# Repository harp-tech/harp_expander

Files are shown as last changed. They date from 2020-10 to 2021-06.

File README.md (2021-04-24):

# Harp Input Expander
# Harp Output Expander

Harp board to expand the inputs and outputs of the current harp ecosystem.

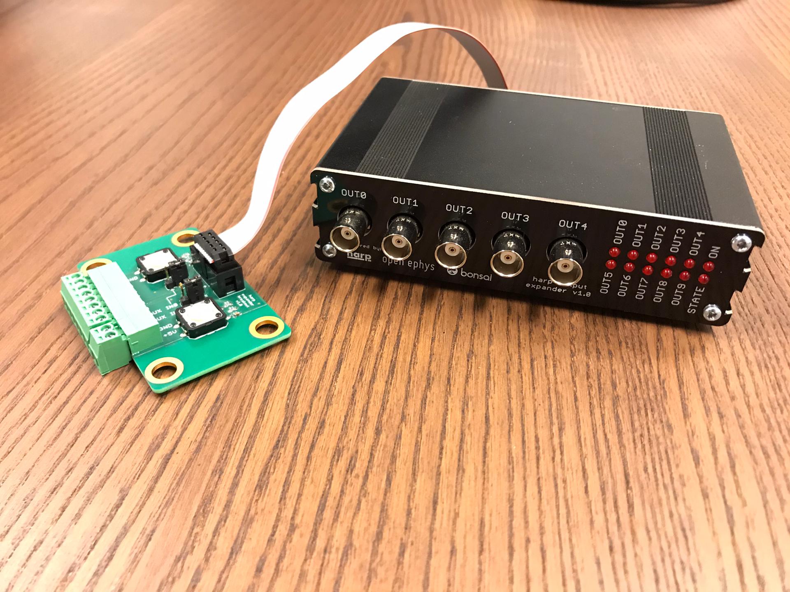
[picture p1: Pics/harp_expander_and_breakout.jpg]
DeviceFront


# Licensing

The code, designs, documentation, and photos available in this repository is free: you can redistribute it and/or modify it under the terms of the used license.
Each subdirectory will contain a license or, possibly, a set of licenses if it involves both hardware and software. Check files named LICENSE.

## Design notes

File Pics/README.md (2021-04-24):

### Licensing
Copyright Filipe Carvalho 2021

<br />Este trabalho está licenciado com uma Licença <a rel="license" href="http://creativecommons.org/licenses/by/4.0/">Creative Commons - Atribuição  4.0 Internacional</a>.

#### You are free to:
*Share* — copy and redistribute the material in any medium or format.

*Adapt* — remix, transform, and build upon the material for any purpose, even commercially.

#### Under the following terms:
*Attribution* — You must give appropriate credit, provide a link to the license, and indicate if changes were made. You may do so in any reasonable manner, but not in any way that suggests the licensor endorses you or your use.

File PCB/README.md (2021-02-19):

# Harp Expander PCB

## Licensing

The designs, documentation, and photos available in this repository are free: you can redistribute it and/or modify it under the terms of the used license.
Check file named LICENSE.

Copyright Filipe Carvalho 2020-2021

<br />This work is licensed under a <a rel="license" href="http://creativecommons.org/licenses/by-nc-sa/3.0/igo/">Creative Commons Attribution-NonCommercial-ShareAlike 3.0 IGO License</a>.

If your are interested in obtaining a license to sell this device, please contact filipe@open-ephys.org

[1]: https://docs.google.com/spreadsheets/d/1aobmmEzBDethzIlrm1eg0eYkBqlyX3s9WbA9KgRwVQI/edit?usp=sharing

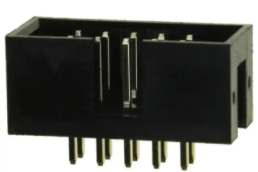
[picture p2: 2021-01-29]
PCB modules/magnetic encoder/mechanical/bottom's connector.bmp

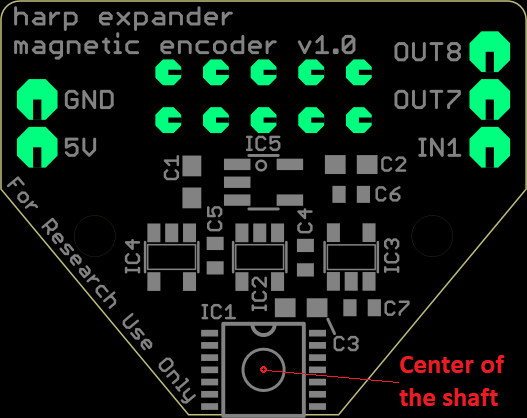
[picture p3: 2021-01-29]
PCB modules/magnetic encoder/mechanical/shaft center.bmp

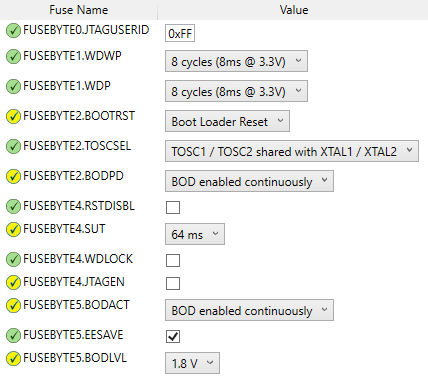
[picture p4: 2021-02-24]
Firmware/Releases/FusesATxmega128A1U (atmel studio 7).bmp

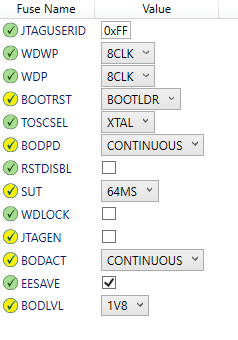
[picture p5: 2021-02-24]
Firmware/Releases/FusesATxmega128A1U.bmp

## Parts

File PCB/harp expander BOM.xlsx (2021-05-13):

Qty | Value | Package | Parts | MPN | Type
PCB COMPONENTS
5 | BNC plug |  | BNC0, BNC1, BNC2, BNC3, BNC4 | 73100-0105 | TH
27 | 100nF | C0402 | C1, C3, C5, C7, C9, C12, C13, C14, C15, C16, C17, C18, C19, C20, C21, C22, C25, C26, C27, C28, C29, C30, C31, C32, C35, C36, C40 | MC0402B104K160CT | SMD
9 | 4.7uF | C0603 | C10, C11, C23, C24, C33, C34, C37, C38, C52 | C1608X6S1C475K080AC | SMD
1 | 4.7nF | C0402 | C2 | 885012205084 | SMD
1 | 100u 25V | TT2D6 | C39 | EEUFM1E101B | TH
2 | 47pF | C0402 | C4, C6 | 04025A470JAT2A | SMD
11 | 330pF | C0402 | C41, C42, C43, C44, C45, C46, C47, C48, C49, C50, C51 | C0402C331J5GACTU | SMD
2 | CLCK_JACK | 35RASMT2BHNTRX | CLKIN, CLKOUT | 35RASMT2BHNTRX | SMD
1 | XMEGA-A1TQFP | TQFP100 | IC1 | ATXMEGA128A1U-AU | SMD
1 | USBLC6-2SC6 | SOT23-6L | IC2 | USBLC6-2SC6 | SMD
1 | FT232RL | SSOP28 | IC3 | FT232RL-REEL | SMD
2 | TLV70033DDCR | TSOT23-5 | IC4, IC5 | TLV70033DDCR | SMD
1 | SI8610BC-B-IS | SO-08 | IC6 | SI8610EC-B-IS | SMD
4 | SN74LVC1G125DBVT | SOT23-5 | IC7, IC8, IC9, IC10 | SN74LVC1G125DBVT | SMD
1 | 40R@100MHz | R0805 | L1 | MI0805K400R-10 | SMD
6 | RED_LEDs | 569-011X-X00_LED_ARRAY | LED0, LED1, LED2, LED3, LED4, LED5 | 5690-111-100F | TH
1 | Oscillator | OSCILLATOR_3.2X2.5 | OSC | O 32,0-JT32C-A-K-3,3-LF | SMD | Alternative: DSC1001CI5-032.0000T
1 | PROG HEADER | MA03-2 | PDI | 67996-206HLF | TH
1 | 10R | R0402 | R2 | CRCW040210R0FKEDHP | SMD
12 | 1k | R0402 | R20, R21, R22, R23, R24, R25, R26, R27, R28, R29, R30, R31 | CRCW04021K00FKED | SMD
31 | 10k | R0402 | R3, R9, R10, R11, R12, R13, R14, R15, R16, R17, R19, R38, R43, R46, R47, R53, R54, R55, R56, R57, R58, R59, R60, R61, R62, R63, R64, R65, R66, R67, R68 | CRCW040210K0FKED | SMD
12 | 330R | R0402 | R32, R33, R34, R35, R36, R37, R39, R40, R41, R42, R44, R45 | RC0402FR-07330RL | SMD
11 | 100R | R0603 | R4, R5, R6, R7, R8, R48, R49, R50, R51, R52, R69 | CRCW0603100RFKEAHP | SMD
1 | I/O Header | ML10L | SV1 | SBH11-PBPC-D05-RA-BK | TH
12 | BC850 | SOT23 | T2, T3, T4, T5, T6, T7, T8, T9, T10, T11, T12, T13 | BC850C,215 | SMD
2 | 744245X | SO24L | U1, U2 | 74LVC4245AD,118 | SMD
1 | 74HCT125SO14 | SO14 | U3 | 74HCT125D,653 | SMD
1 | mini USB | 240-0002-1 | USB | UX60-MB-5S8 | SMD
1 |  |  | PCB
POST-PRODUCTION
1 |  |  | Front Panel PCB | PCBWAY
1 |  |  | Rear Panel PCB | PCBWAY
1 |  |  | Enclosure | B5-080BK
4 |  |  | Bumper Cylindrical Dome 9.53mm | SJ-5306-CLEAR-3000/CASE
ACCESSORIES
1 |  |  | 3.5mm stereo jack cable 1.2 m, Black | AV13646
1 |  |  | 0.9 left angle USB cable | USB2HABM3RA
NOTES
 |  |  |  | Number of unique parts | 28
 |  |  |  | Number of unique SMD parts | 23
 |  |  |  | Number of unique TH parts | 5
 |  |  |  | Number of SMD parts | 147
 |  |  |  | Number of TH parts | 14
 |  | Optional
 |  | Holder: MF80BK2

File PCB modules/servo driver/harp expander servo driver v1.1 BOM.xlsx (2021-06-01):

Qty | Value | Package | Parts | MPN | Type | Distributor | Distributor PN
ASSEMBLY HOUSE
2 | SI8641AB-B-IS | SO16W | U1, U2 | SI8641AB-B-IS | SMD | Digikey | SI8641AB-B-IS-ND
1 | LT1765 | TSSOP16 | U3 | LT1765EFE#TRPBF | SMD | Digikey | LT1765EFE#TRPBFCT-ND
1 | NCP718XSN500 | SOT23-5 | U4 | NCP718BSN500T1G | SMD | Digikey | NCP718BSN500T1GOSCT-ND
6 | 100nF | C0402 | C1, C2, C3, C4, C5, C6 | CGA2B3X7R1H104K050BB | SMD | Digikey | 445-6899-2-ND
1 | 10uF | C0603 | C10 | EMK107BBJ106MA-T | SMD | Digikey | 587-3238-1-ND
2 | 2.2uF | C0603 | C7, C11 | GRM188R61E225MA12D | SMD | Digikey | 490-12738-1-ND
1 | 2.2nF | C0402 | C8 | CL05B222JB5NNNC | SMD | Digikey | 1276-1532-6-ND
1 | 180nF | C0603 | C9 | GCG188R91H184KA01D | SMD | Digikey | 490-GCG188R91H184KA01DCT-ND
1 | 40.2k | R0402 | R1 | RC0402FR-0740K2L | SMD | Digikey | 311-40.2KLRCT-ND
2 | 10k | R0402 | R2, R3 | CRCW040210K0FKEDC | SMD | Digikey | 541-3959-1-ND
1 | SSB43L-E3 | SMB | D1 | SSB43L-E3/52T | SMD | Digikey | SSB43L-E3/52TGICT-ND
1 | CMDSH-3 | SOD323-R | D2 | CMDSH-3 | SMD | Digikey | 1514-CMDSH-3TRPBFREECT-ND
1 | 10uH 3A | COILCRAFT_1 | L3 | IHLP2525CZER100M01 | SMD | Digikey | 541-1013-2-ND
1 | DC_JACK2.1MM | DC_POWER_INPUT_2.1MM | PWR1 | 163-179PH-EX | TH | Mouser | 163-179PH-EX
3 | CON_3.5MM_1X3 | CON_3.5MM_1X3 | X1, X2, X3 | 691322110003 | TH | Digikey | 732-2770-ND
1 | aux_header | FE06 | X4 | n.a. | - | - | n.a.
1 | IDC 10WAY STRAIGHT | PAK100/2500-10 | X5 | SBH11-PBPC-D05-ST-BK | TH | Digikey | S9169-ND
POST-PRODUCTION
3 | TERMINAL BLOBK PLUG 3WAY | - | n.a. | 691361100003 | - | Digikey | 732-2752-ND | to build step motor cable
2 | CNTR PLRZD RECPT 10P | - | n.a. | 1658621-1 | - | Digikey | AKC10H-ND | to build 0.5m control cable
1 | 10 COND. 28AWG ROUND 1PC=100FT | - | n.a. | 3365/10 100 | - | Digikey | 3M157849-100-ND | to build 0.5m control cable
NOTES
 |  |  |  | Number of unique parts | 16
 |  |  |  | Number of SMD parts | 21
 |  |  |  | Number of TH parts | 5

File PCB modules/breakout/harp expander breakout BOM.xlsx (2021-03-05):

Qty | Value | Package | Parts | MPN | Type
ASSEMBLY HOUSE
2 | 2.2k 100mW | R0603 | R1, R2 | ERJ3GEYJ222V | SMD
2 | 4.3k 100mW | R0603 | R3, R4 | ERJ3GEYJ432V | SMD
2 | 1uF 25V | C0603 | C1, C2 | CL10A105KA8NNNC | SMD
2 | SWITCH |  | SW0, SW1 | B3F-4000 | TH
2 | JUMPER 3WAY |  | JP1, JP2 | 68001-203HLF | TH
1 | IDC 10WAY STRAIGHT |  | SV1 | SBH11-PBPC-D05-ST-BK | TH
1 | TERMINAL BLOCK 8WAY |  | SV2 | 691322110008 | TH
1 | TERMINAL BLOCK 2WAY |  | SV3 | 691322110002 | TH
POST-PRODUCTION
1 | TERMINAL BLOCK PLUG 8WAY |  |  | 691361100008
1 | TERMINAL BLOCK PLUG 2WAY |  |  | 691361100002
2 | CNTR PLRZD RECPT 10P |  |  | 1658621-1
2 | JUMPER |  |  | SNT-100-BK-T
 | 10 COND. 28AWG ROUND 1PC=100FT |  |  | 3365/10 100 |  | To create a cable with 0.5 meters
NOTES
 |  |  |  | Number of unique parts | 8
 |  |  |  | Number of SMD parts | 6
 |  |  |  | Number of TH parts | 7

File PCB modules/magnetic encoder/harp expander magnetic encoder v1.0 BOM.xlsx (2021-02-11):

Qty | Value | Package | Parts | MPN | Type | Distributor | Distributor PN
ASSEMBLY HOUSE
3 | 10uF 16V X5R 20% | C0603 | C1, C2, C3 | EMK107BBJ106MA-T | SMD | Digikey | 587-3238-6-ND
4 | 100nF 50V X7R 10% | C0402 | C4, C5, C6, C7 | CGA2B3X7R1H104K050BB | SMD | Digikey | 445-6899-6-ND
3 | Single Bus Buffer Gate | SOT-23-5 | IC2, IC3, IC4 | SN74LVC1G125DBVT | SMD | Digikey | 296-26595-6-ND
1 | Magnetic Rotary Encoder 14 bits | 14-TSSOP | IC1 | AS5048A-HTSP-500 | SMD | Digikey | AS5048A-HTSP-500DKR-ND
1 | Ultra-Low-Noise LDO 3.3V 250mA | SOT-23-5 | IC5 | LP5907MFX-3.3/NOPB | SMD | Digikey | 296-38557-6-ND
1 | IDC 10WAY STRAIGHT | PAK100/2500-10 | SV1 | SBH11-PBPC-D05-ST-BK | TH | Digikey | S9169-ND
POST-PRODUCTION
2 | CNTR PLRZD RECPT 10P |  |  | 1658621-1 | - | Digikey | AKC10H-ND
 | 10 COND. 28AWG ROUND 1PC=100FT |  |  | 3365/10 100 | - | Digikey | 3M157849-100-ND | to build 0.5m control cable
NOTES
 |  |  |  | Number of unique parts | 6
 |  |  |  | Number of SMD parts | 12
 |  |  |  | Number of TH parts | 1

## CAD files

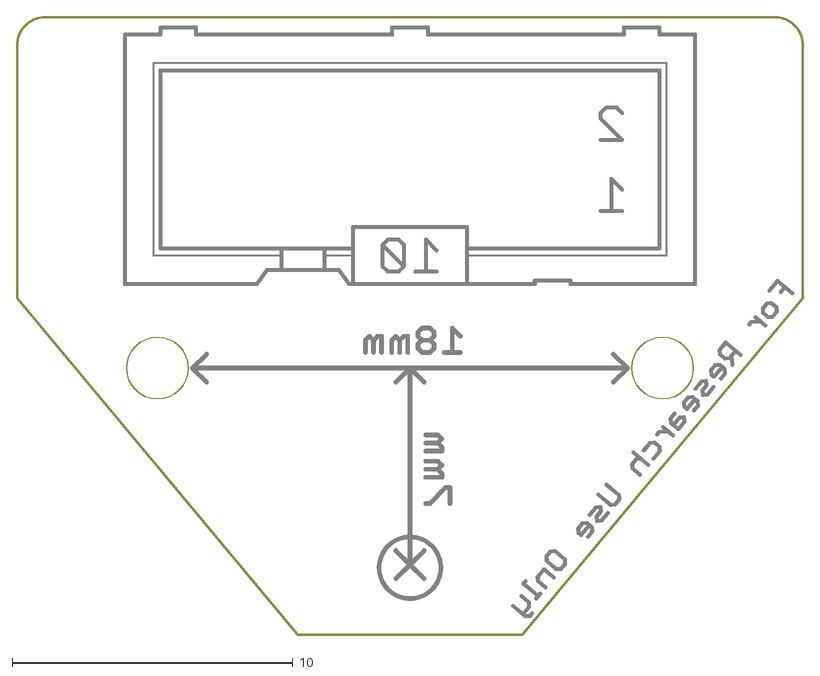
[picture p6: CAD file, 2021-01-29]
PCB modules/magnetic encoder/mechanical/harp expander magnetic encoder v1.0 - bottom.dxf
28.1 x 22.1

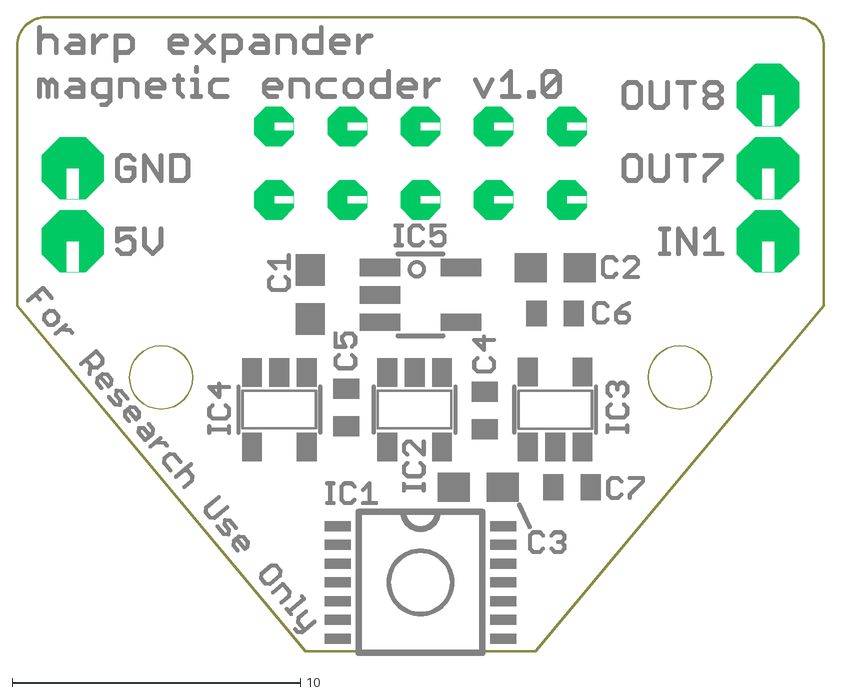
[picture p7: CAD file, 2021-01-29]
PCB modules/magnetic encoder/mechanical/harp expander magnetic encoder v1.0 - top.dxf
28.1 x 22.2

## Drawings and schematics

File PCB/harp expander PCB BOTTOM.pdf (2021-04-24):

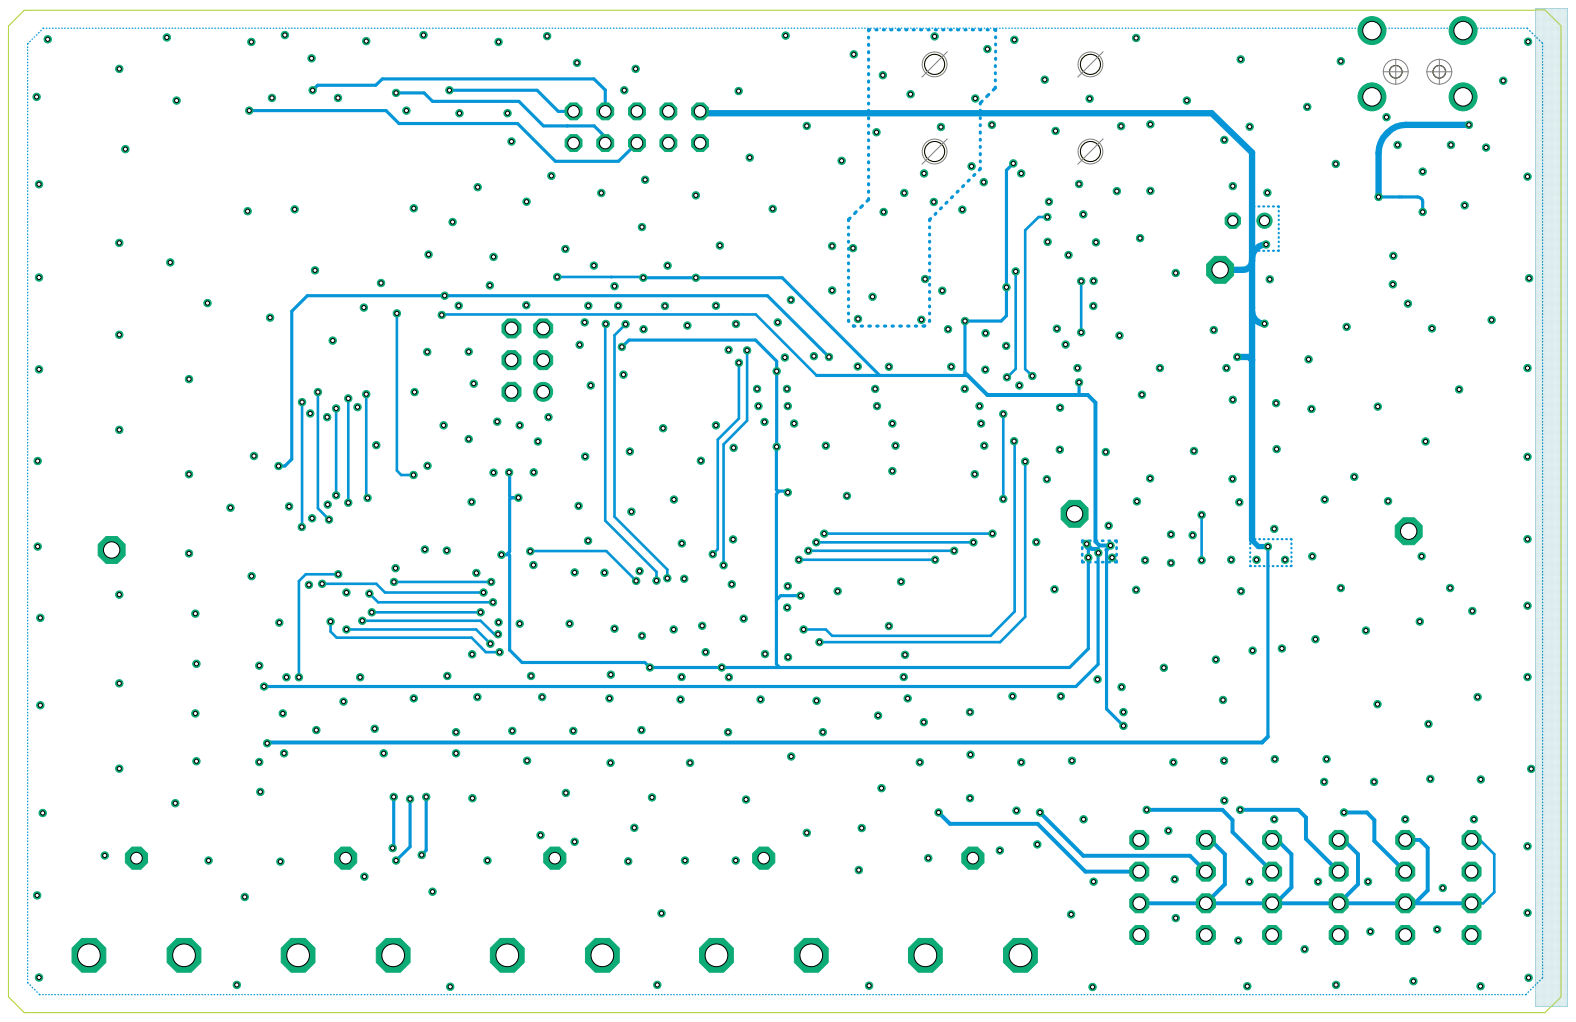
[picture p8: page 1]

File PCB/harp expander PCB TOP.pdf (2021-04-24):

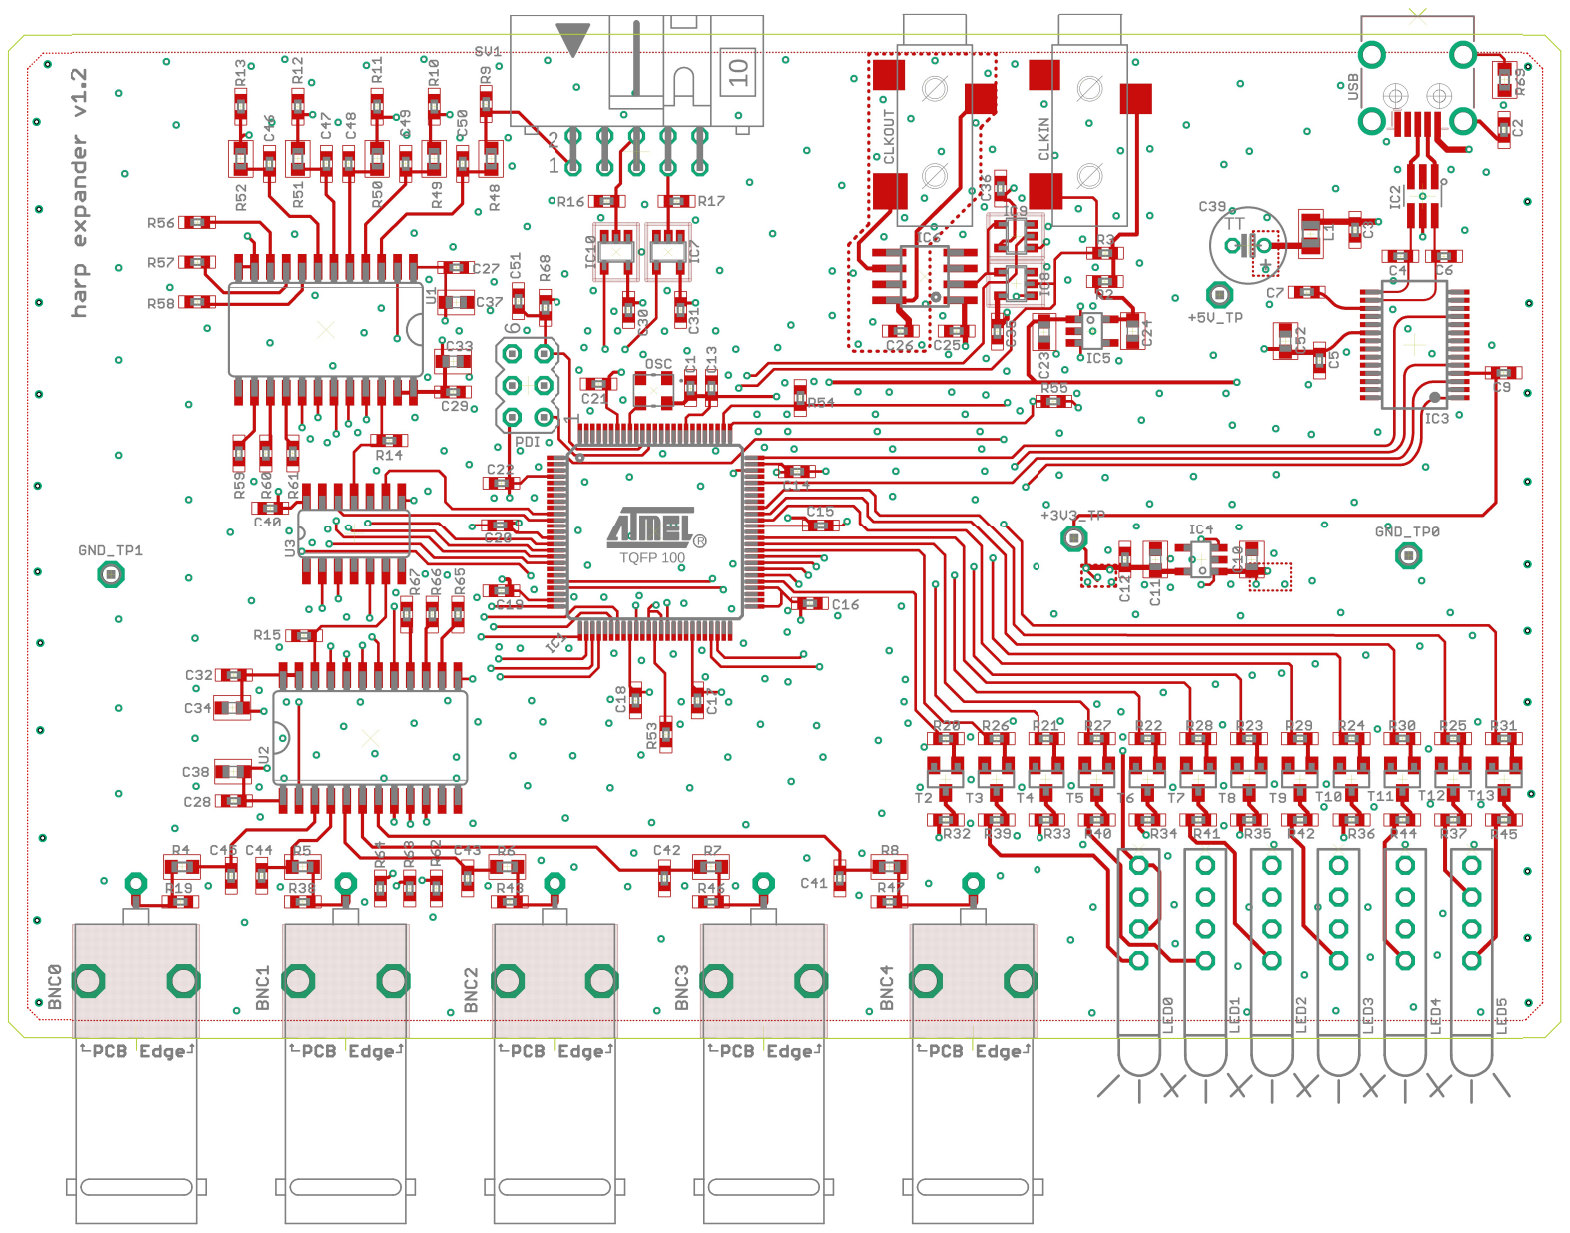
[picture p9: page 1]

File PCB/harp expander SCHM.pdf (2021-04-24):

# PF7(TXD1/SCK) 52 GND 33 GND 43

A

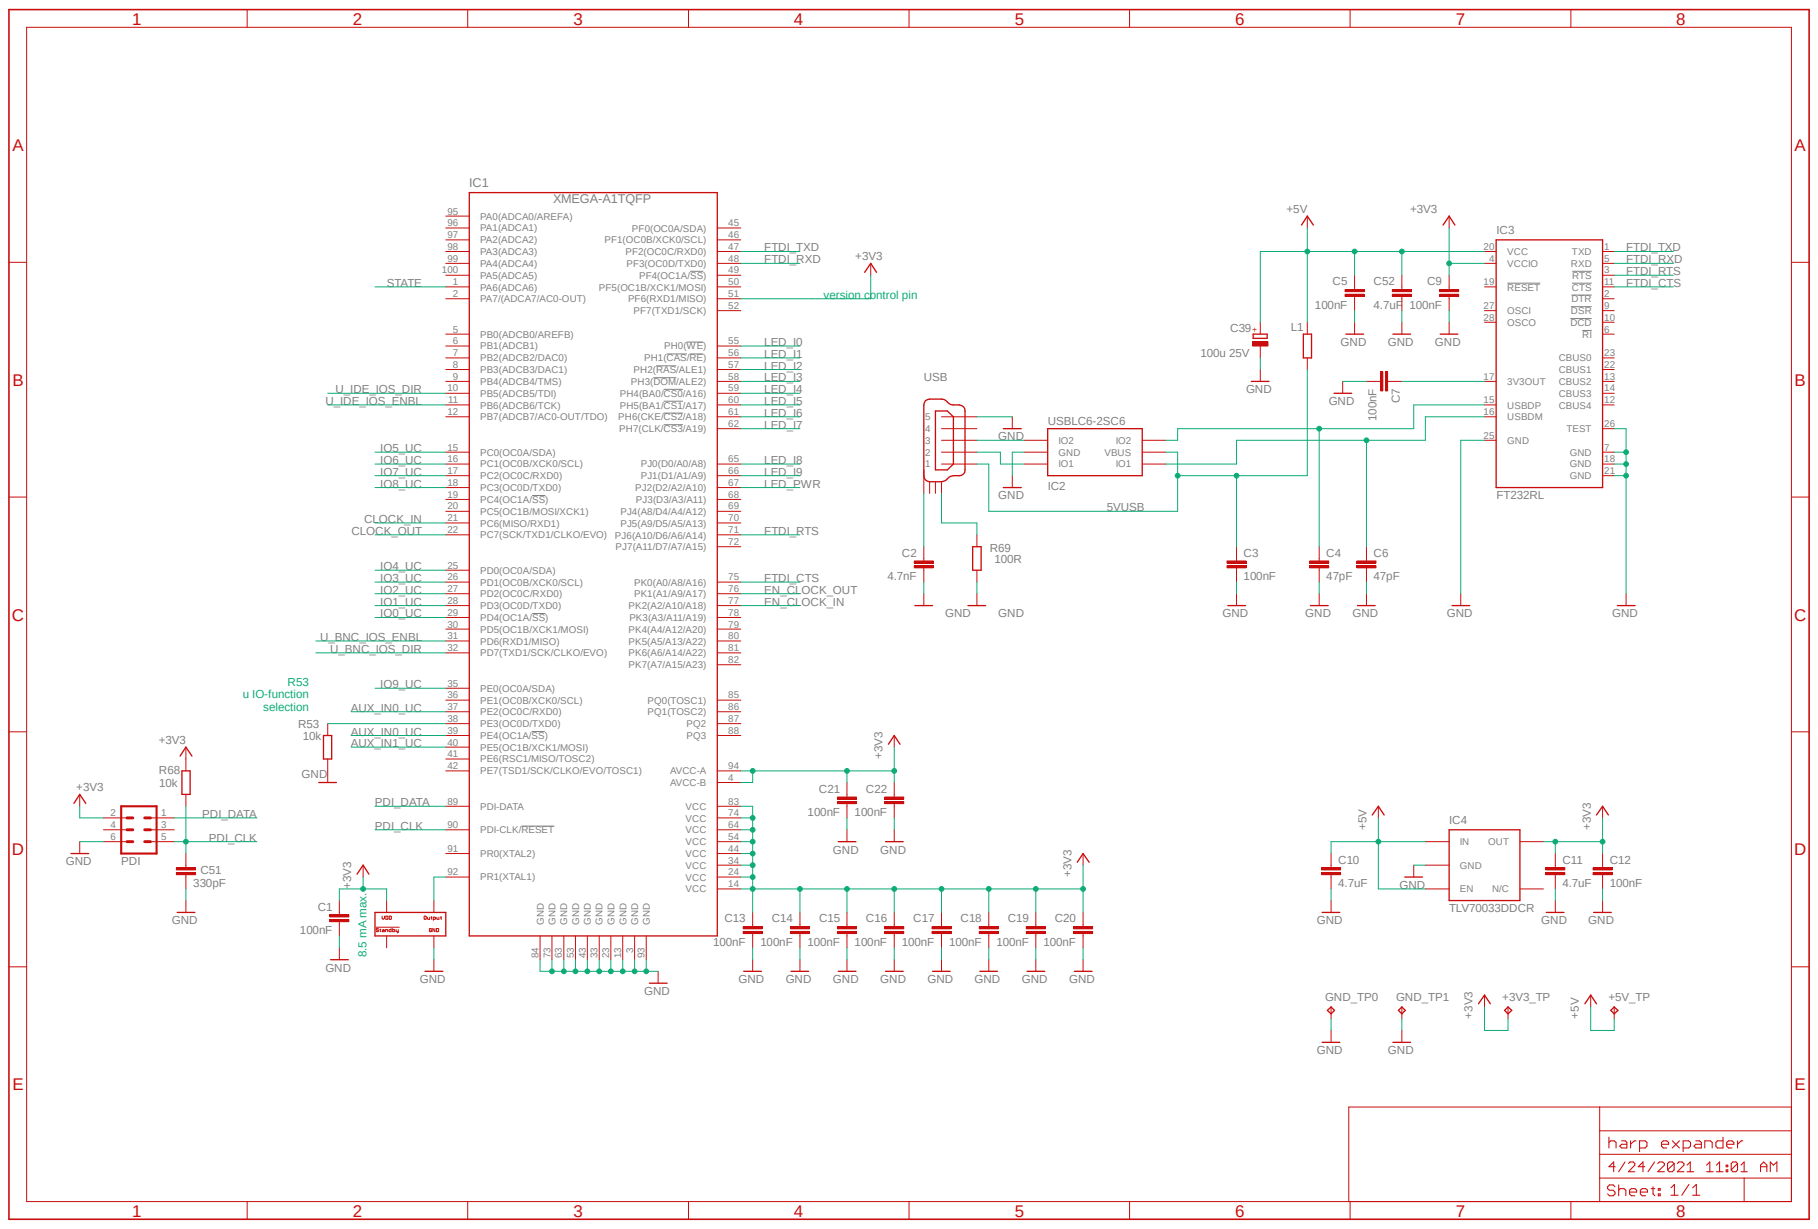
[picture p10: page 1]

A

A

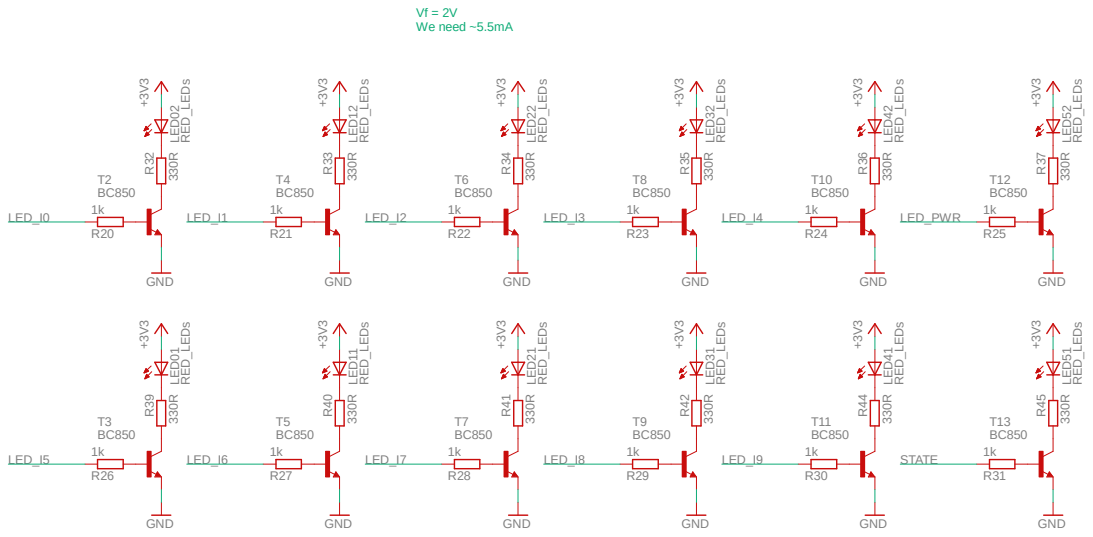
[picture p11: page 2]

A

A

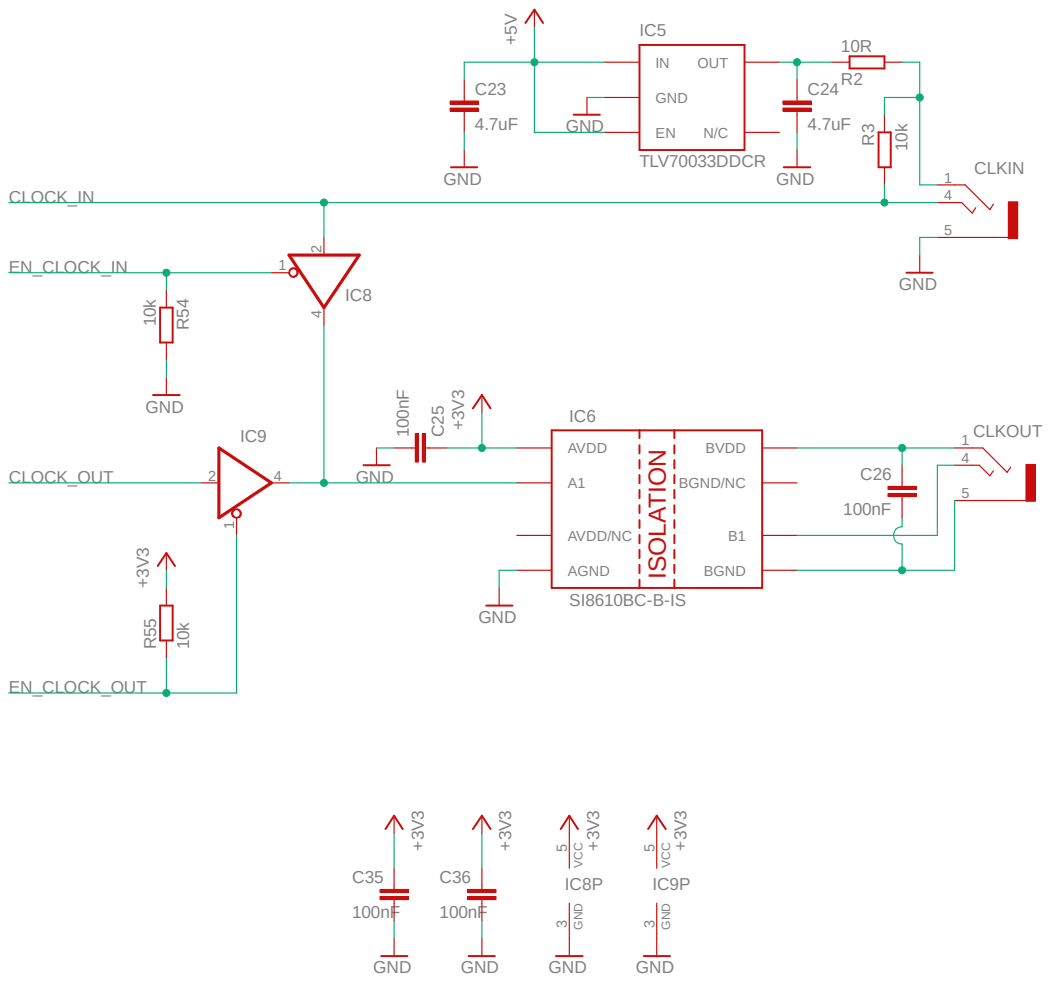
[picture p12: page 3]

# GND +3V³ +3V³

# GND 10k

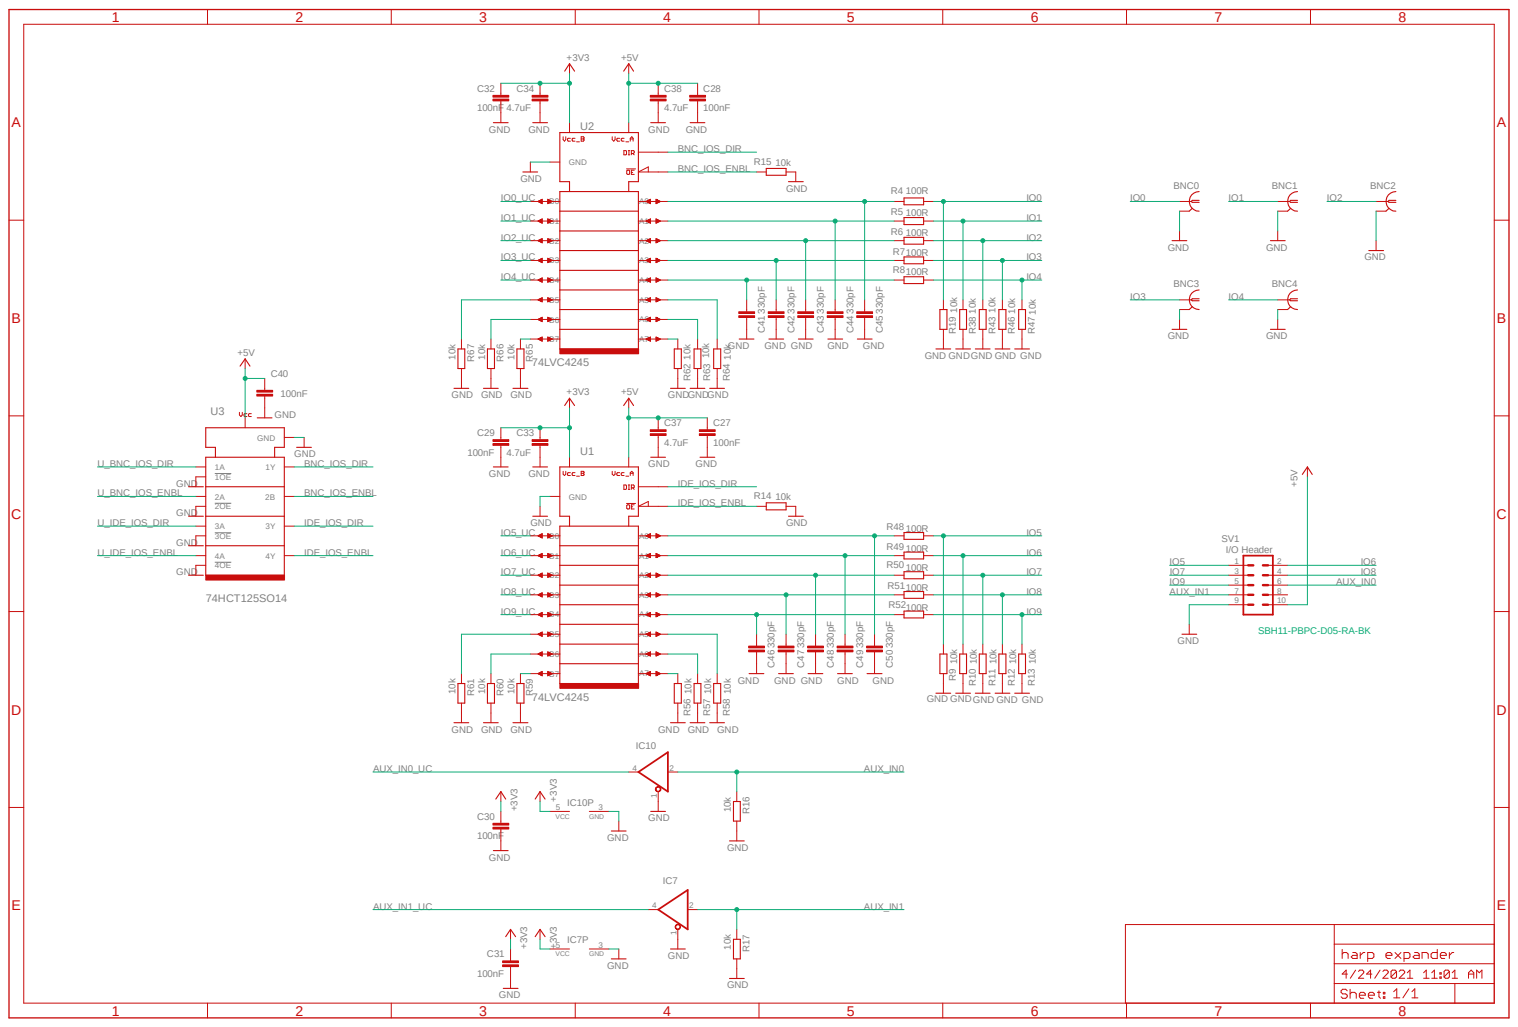
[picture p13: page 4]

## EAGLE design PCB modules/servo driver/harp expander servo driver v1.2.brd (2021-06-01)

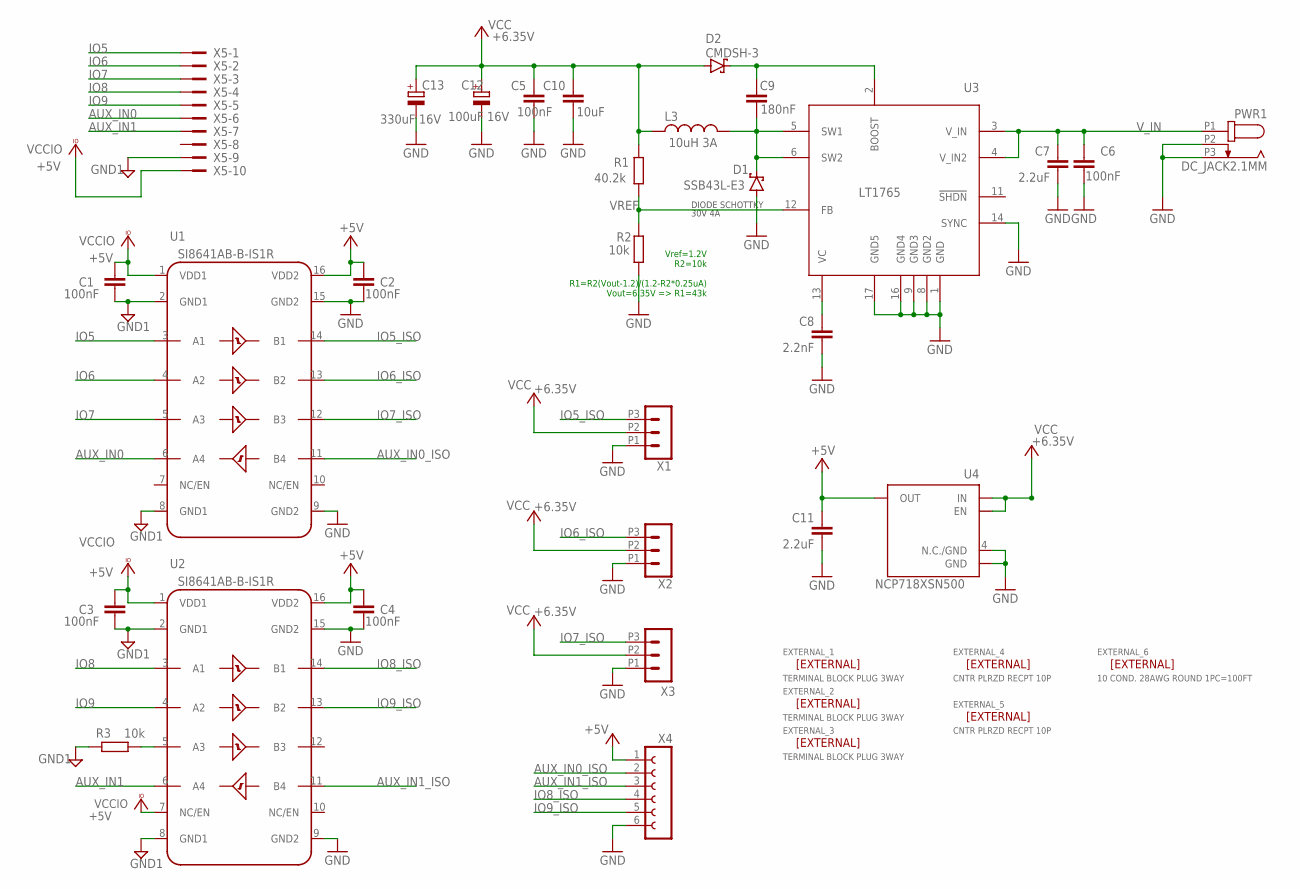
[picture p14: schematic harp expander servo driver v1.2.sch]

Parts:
C1, C2, C3, C4, C5, C6: 100nF; C0402; MPN CGA2B3X7R1H104K050BB; DIGIKEY_PN 445-6899-2-ND
C7, C11: 2.2uF; C0603; MPN GRM188R61E225MA12D; DIGIKEY_PN 490-12738-1-ND
C8: 2.2nF; C0402; MPN CL05B222JB5NNNC; DIGIKEY_PN 1276-1532-6-ND
C9: 180nF; C0603; MPN GCG188R91H184KA01D; DIGIKEY_PN 490-GCG188R91H184KA01DCT-ND
C10: 10uF; C0603; MPN EMK107BBJ106MA-T; DIGIKEY_PN 587-3238-1-ND
C12: 100uF 16V; CT7343; MPN T491D107K016AT7280; DIGIKEY_PN 399-18066-1-ND
C13: 330uF 16V; E3,5-8; MPN MCMR16V337M8X7; FARNELL_PN 1870957
D1: SSB43L-E3; SMB; MPN SSB43L-E3/52T; DIGIKEY_PN SSB43L-E3/52TGICT-ND
D2: CMDSH-3; SOD323-R; MPN CMDSH-3; DIGIKEY_PN 1514-CMDSH-3TRPBFREECT-ND
EXTERNAL_1, EXTERNAL_2, EXTERNAL_3: TERMINAL BLOCK PLUG 3WAY; -; MPN 691361100003; DIGIKEY_PN 732-2752-ND
EXTERNAL_4, EXTERNAL_5: CNTR PLRZD RECPT 10P; -; MPN 1658621-1; DIGIKEY_PN AKC10H-ND
EXTERNAL_6: 10 COND. 28AWG ROUND 1PC=100FT; -; MPN 3365/10 100; DIGIKEY_PN 3M157849-100-ND
L3: 10uH 3A; L_IHLP_PADS; MOUSER_PN 70-IHLP2525CZER100M0; DIGIKEY_PN 541-1013-2-ND
PWR1: DC_JACK2.1MM; DC_POWER_INPUT_2.1MM; MPN 163-179PH-EX; DIGIKEY_PN 163-179PH-EX MOUSER
R1: 40.2k; R0402; MPN RC0402FR-0740K2L; DIGIKEY_PN 311-40.2KLRCT-ND
R2, R3: 10k; R0402; MPN CRCW040210K0FKEDC; DIGIKEY_PN 541-3959-1-ND
U1, U2: SI8641AB-B-IS1R; SO16W; MOUSER_PN 634-SI8641AB-B-IS1R; DIGIKEY_PN SI8641AB-B-IS-ND
U3: LT1765; TSSOP16; MPN LT1765EFE#TRPBF; DIGIKEY_PN LT1765EFE#TRPBFCT-ND
U4: NCP718XSN500; SOT23-5; MPN NCP718BSN500T1G; DIGIKEY_PN NCP718BSN500T1GOSCT-ND
X1, X2, X3: CON_3.5MM_1X3; MPN 691322110003; DIGIKEY_PN 732-2770-ND
X4: aux_header; FE06; MPN n.a.
X5: IDC 10WAY STRAIGHT; PAK100/2500-10; MPN SBH11-PBPC-D05-ST-BK; DIGIKEY_PN S9169-ND

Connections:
+5V: C2.1, C4.1, C11.1, U1.16 (VDD2), U2.16 (VDD2), U4.5 (OUT), X4.1
AUX_IN0: U1.6 (A4), X5.6
AUX_IN0_ISO: U1.11 (B4), X4.2
AUX_IN1: U2.6 (A4), X5.7
AUX_IN1_ISO: U2.11 (B4), X4.3
GND: C2.2, C4.2, C5.2, C6.2, C7.2, C8.2, C10.2, C11.2, C12.-, C13.-, D1.A, PWR1.P2 (2), PWR1.P3 (3), R2.1, U1.9 (GND2), U1.15 (GND2), U2.9 (GND2), U2.15 (GND2), U3.1 (GND), U3.8 (GND2), U3.9 (GND3), U3.14 (SYNC), U3.16 (GND4), U3.17 (GND5), U4.2 (GND), U4.4 (N.C./GND), X1.P1 (1), X2.P1 (1), X3.P1 (1), X4.6
GND1: C1.2, C3.2, R3.2, U1.2 (GND1), U1.8 (GND1), U2.2 (GND1), U2.8 (GND1), X5.9
IO5: U1.3 (A1), X5.1
IO5_ISO: U1.14 (B1), X1.P3 (3)
IO6: U1.4 (A2), X5.2
IO6_ISO: U1.13 (B2), X2.P3 (3)
IO7: U1.5 (A3), X5.3
IO7_ISO: U1.12 (B3), X3.P3 (3)
IO8: U2.3 (A1), X5.4
IO8_ISO: U2.14 (B1), X4.4
IO9: U2.4 (A2), X5.5
IO9_ISO: U2.13 (B2), X4.5
unnamed: R3.1, U2.5 (A3)
unnamed: C8.1, U3.13 (VC)
unnamed: C9.2, D1.C, L3.2, U3.5 (SW1), U3.6 (SW2)
unnamed: C9.1, D2.C, U3.2 (BOOST)
VCC: C5.1, C10.1, C12.+, C13.+, D2.A, L3.1, R1.2, U4.1 (IN), U4.3 (EN), X1.P2 (2), X2.P2 (2), X3.P2 (2)
VCCIO: C1.1, C3.1, U1.1 (VDD1), U2.1 (VDD1), U2.7 (NC/EN), X5.10
VREF: R1.1, R2.2, U3.12 (FB)
V_IN: C6.1, C7.1, PWR1.P1 (1), U3.3 (V_IN), U3.4 (V_IN2)

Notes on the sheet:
Vref=1.2V R2=10k R1=R2(Vout-1.2)/(1.2-R2*0.25uA) Vout=6.35V => R1=43k
DIODE SCHOTTKY 30V 4A

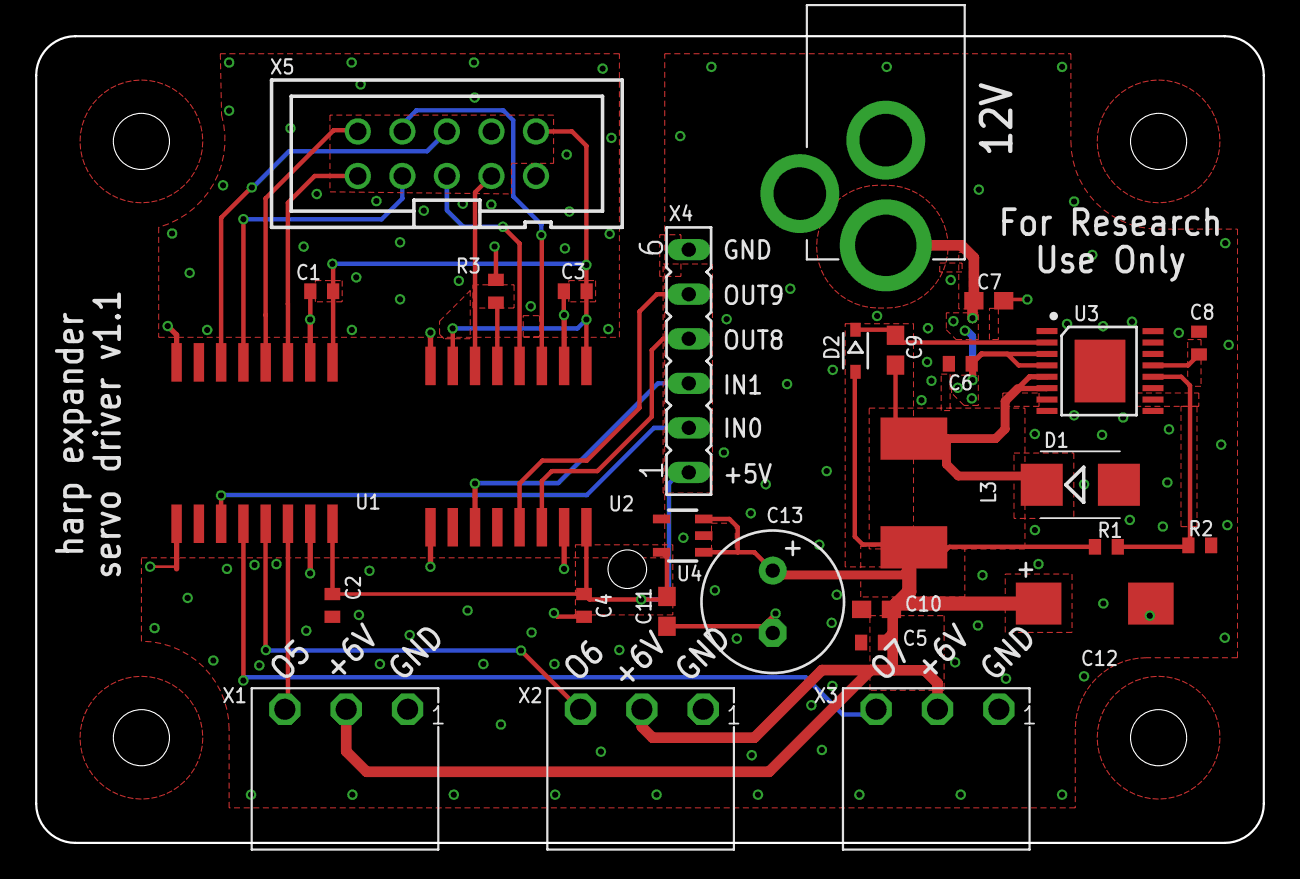
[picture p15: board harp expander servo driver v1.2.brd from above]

Board: 2 copper layers, 70.0 x 46.0 mm, 35 parts (0 on the bottom side), 25 nets.

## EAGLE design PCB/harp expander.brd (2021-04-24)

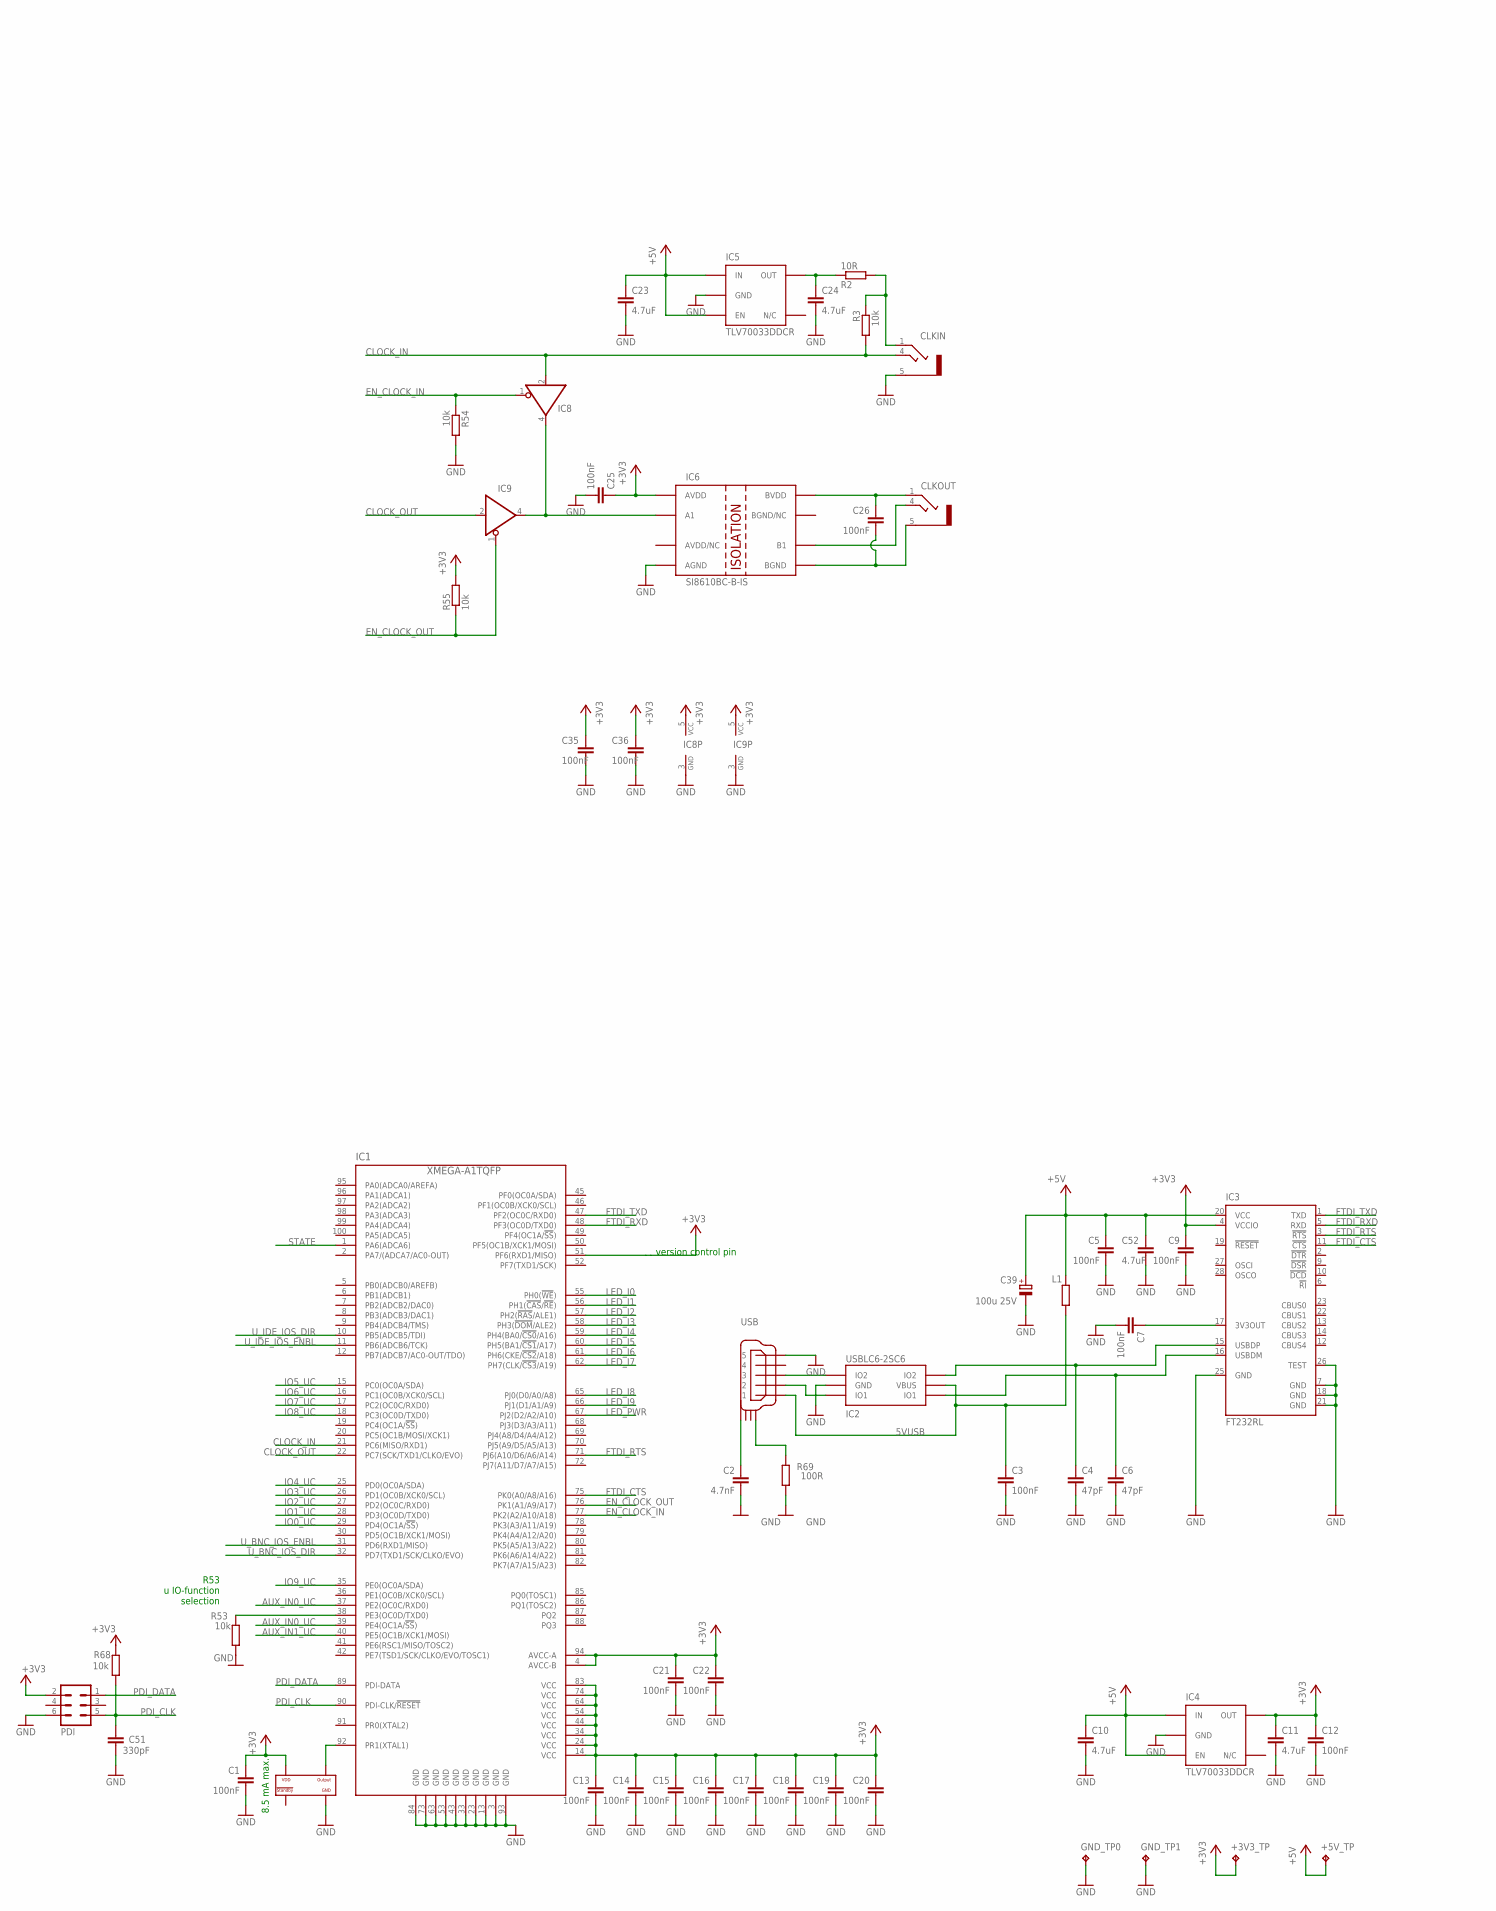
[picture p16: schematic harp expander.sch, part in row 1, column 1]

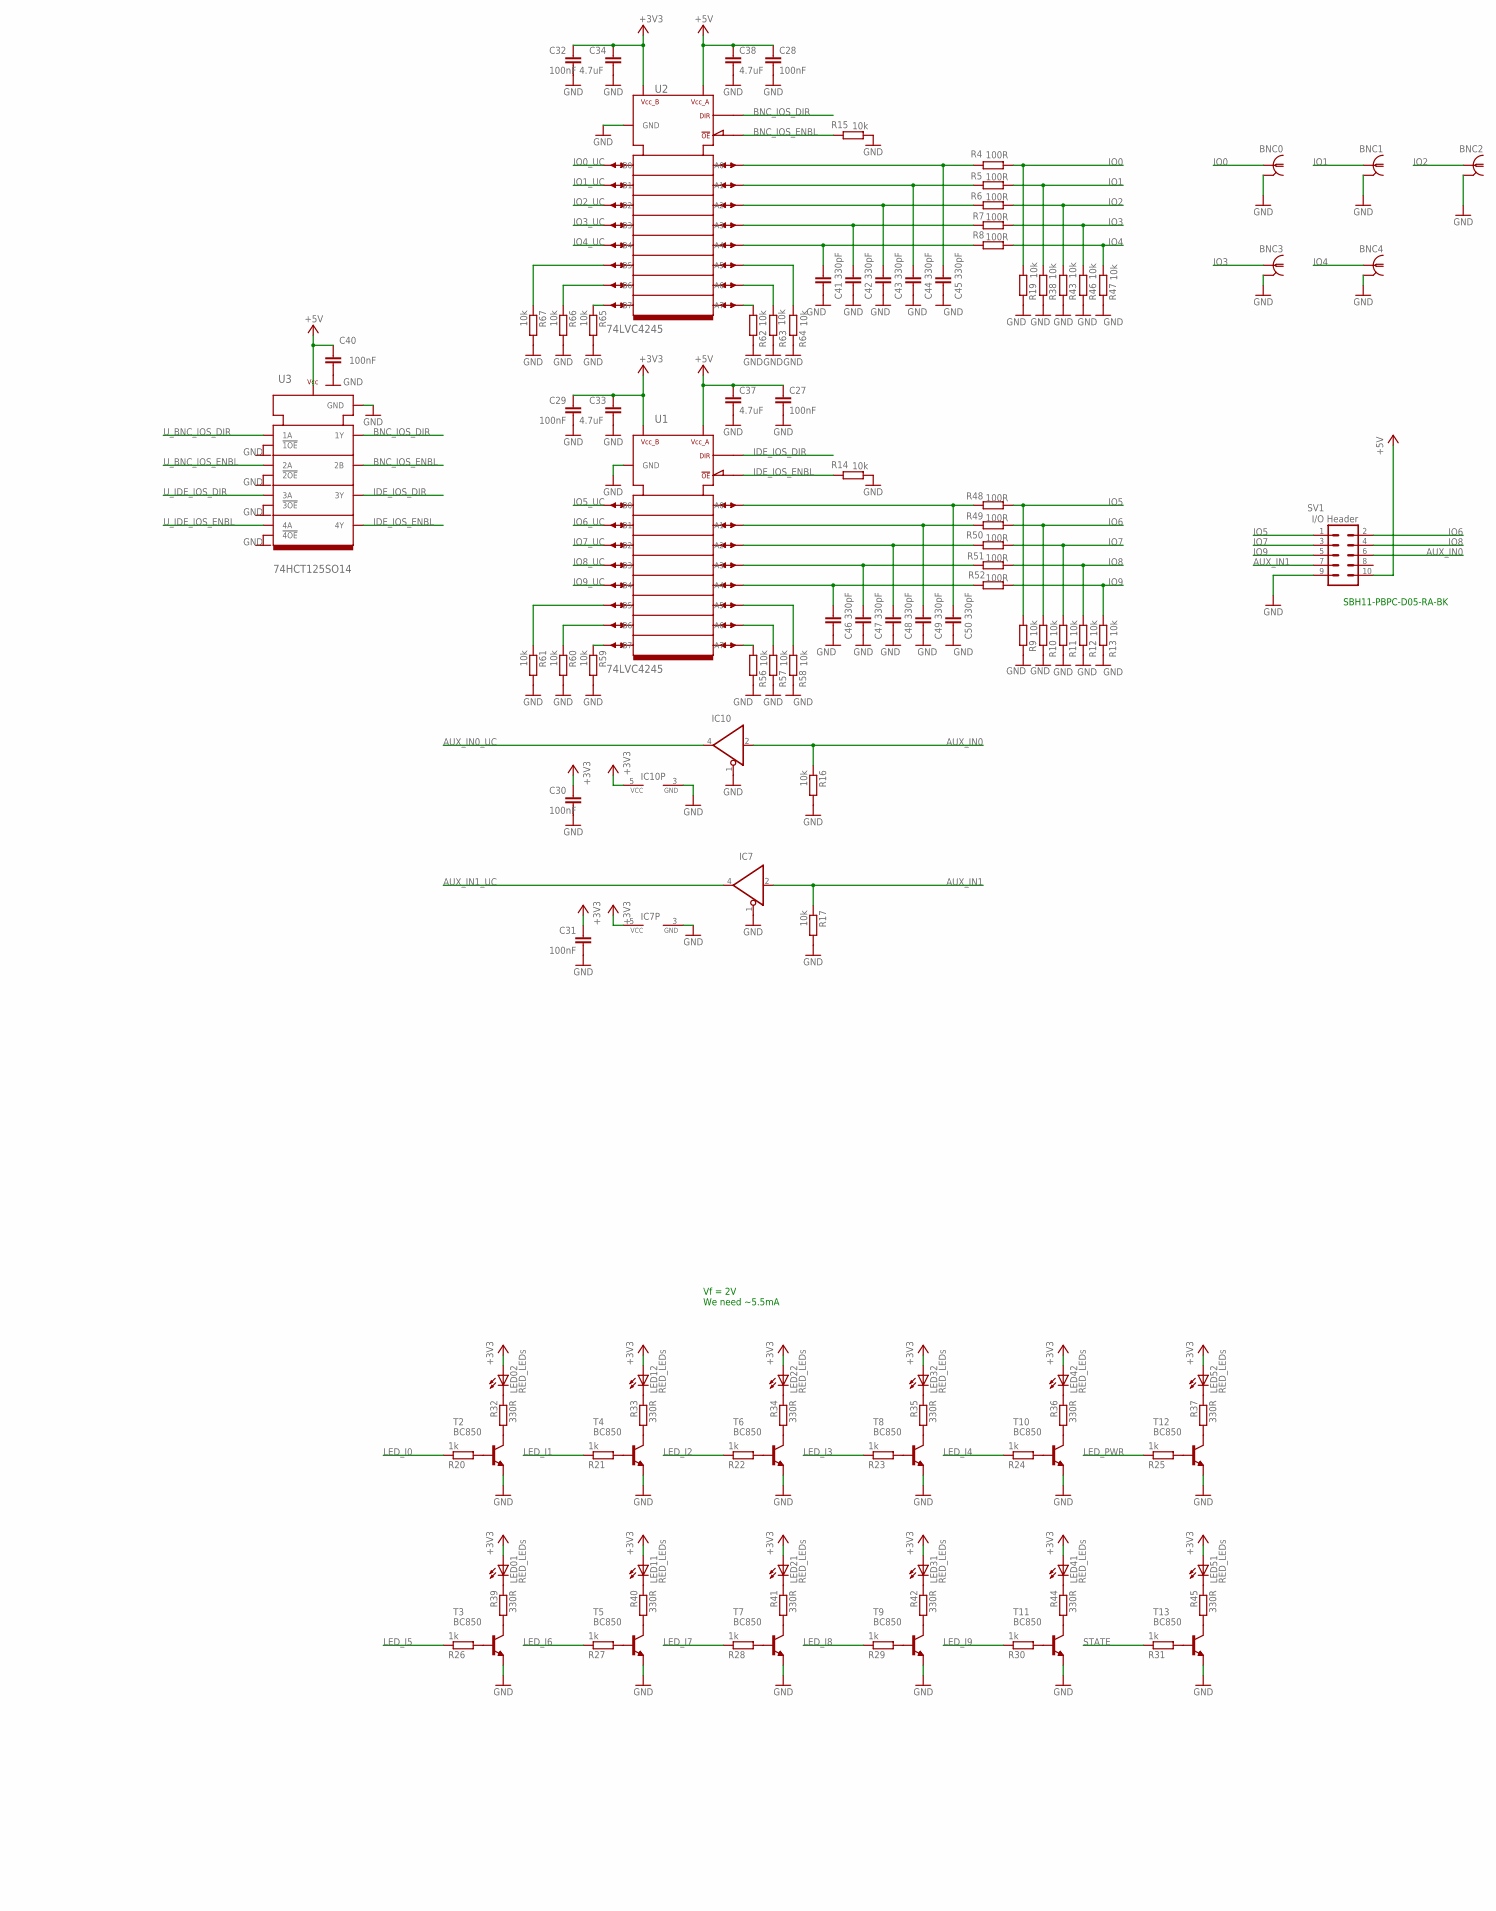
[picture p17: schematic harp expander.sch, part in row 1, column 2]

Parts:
+3V3_TP, +5V_TP: TPPAD1-13; P1-13; MPN n.a.
BNC0, BNC1, BNC2, BNC3, BNC4: BNC plug; 0731000105; MPN 73100-0105
C1, C3, C5, C7, C9, C12, C13, C14, C15, C16, C17, C18, C19, C20, C21, C22, C25, C26, C27, C28, C29, C30, C31, C32, C35, C36, C40: 100nF; C0402; MPN MC0402B104K160CT
C2: 4.7nF; C0402; MPN 885012205084
C4, C6: 47pF; C0402; MPN 04025A470JAT2A
C10, C11, C23, C24, C33, C34, C37, C38, C52: 4.7uF; C0603; MPN C1608X6S1C475K080AC
C39: 100u 25V; TT2D6; MPN EEUFM1E101B
C41, C42, C43, C44, C45, C46, C47, C48, C49, C50, C51: 330pF; C0402; MPN C0402C331J5GACTU
CLKIN: CLCK_JACK; 35RASMT2BHNTRX; MPN 35RASMT2BHNTRX
CLKOUT: CLCK_JACK; 35RASMT2BHNTRX; MPN 35RASMT2BHNTRX
GND_TP0, GND_TP1: TPPAD1-13; P1-13; MPN n.a.
IC1: XMEGA-A1TQFP; TQFP100; MPN ATXMEGA128A1U-AU
IC2: USBLC6-2SC6; SOT23-6L; MPN USBLC6-2SC6
IC3: FT232RL; SSOP28; MPN FT232RL-REEL
IC4, IC5: TLV70033DDCR; TSOT23-5; MPN TLV70033DDCR
IC6: SI8610BC-B-IS; SO-08; MPN SI8610EC-B-IS
IC7, IC8, IC9, IC10: SN74LVC1G125DBVT; SOT23-5; MPN SN74LVC1G125DBVT
L1: 40R@100MHz; R0805; MPN MI0805K400R-10
LED0, LED1, LED2, LED3, LED4, LED5: RED_LEDs; 569-011X-X00_LED_ARRAY; MPN 5690-111-100F
OSC: Oscillator; OSCILLATOR_3.2X2.5; MPN O 32,0-JT32C-A-K-3,3-LF
PDI: PROG HEADER; MA03-2; MPN 67996-206HLF
R2: 10R; R0402; MPN CRCW040210R0FKEDHP
R3, R9, R10, R11, R12, R13, R14, R15, R16, R17, R19, R38, R43, R46, R47, R53, R54, R55, R56, R57, R58, R59, R60, R61, R62, R63, R64, R65, R66, R67, R68: 10k; R0402; MPN CRCW040210K0FKED
R4, R5, R6, R7, R8, R48, R49, R50, R51, R52, R69: 100R; R0603; MPN CRCW0603100RFKEAHP
R20, R21, R22, R23, R24, R25, R26, R27, R28, R29, R30, R31: 1k; R0402; MPN CRCW04021K00FKED
R32, R33, R34, R35, R36, R37, R39, R40, R41, R42, R44, R45: 330R; R0402; MPN RC0402FR-07330RL
SV1: I/O Header; ML10L; MPN SBH11-PBPC-D05-RA-BK
T2, T3, T4, T5, T6, T7, T8, T9, T10, T11, T12, T13: BC850; SOT23; MPN BC850C,215
U1, U2: 744245X; SO24L; MPN 74LVC4245AD,118
U3: 74HCT125SO14; SO14; MPN 74HCT125D,653
USB: mini USB; 240-0002-1; MPN UX60-MB-5S8

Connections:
5VUSB: C3.1, IC2.P$5 (VBUS), L1.2, USB.P$1 (1)
+3V3: +3V3_TP.TP, C1.1, C9.1, C11.1, C12.1, C13.1, C14.1, C15.1, C16.1, C17.1, C18.1, C19.1, C20.1, C21.1, C22.1, C25.1, C29.1, C30.1, C31.1, C32.1, C33.1, C34.1, C35.1, C36.1, IC1.4 (AVCC-B), IC1.14 (VCC), IC1.24 (VCC), IC1.34 (VCC), IC1.44 (VCC), IC1.51 (PF6(RXD1/MISO)), IC1.54 (VCC), IC1.64 (VCC), IC1.74 (VCC), IC1.83 (VCC), IC1.94 (AVCC-A), IC3.4 (VCCIO), IC4.5 (OUT), IC6.1 (AVDD), IC7.5 (VCC), IC8.5 (VCC), IC9.5 (VCC), IC10.5 (VCC), LED0.A1 (A), LED0.A2 (A), LED1.A1 (A), LED1.A2 (A), LED2.A1 (A), LED2.A2 (A), LED3.A1 (A), LED3.A2 (A), LED4.A1 (A), LED4.A2 (A), LED5.A1 (A), LED5.A2 (A), OSC.P$4 (VDD), PDI.2, R55.2, R68.2, U1.23 (VCC_B), U1.24 (VCC_B), U2.23 (VCC_B), U2.24 (VCC_B)
+5V: +5V_TP.TP, C5.1, C10.1, C23.1, C27.1, C28.1, C37.1, C38.1, C39.+, C40.1, C52.1, IC3.20 (VCC), IC4.1 (IN), IC4.3 (EN), IC5.1 (IN), IC5.3 (EN), L1.1, SV1.10, U1.1 (VCC_A), U2.1 (VCC_A), U3.14 (VCC)
AUX_IN0: IC10.2 (I), R16.1, SV1.6
AUX_IN0_UC: IC1.37 (PE2(OC0C/RXD0)), IC1.39 (PE4(OC1A/!SS!)), IC10.4 (O)
AUX_IN1: IC7.2 (I), R17.1, SV1.7
AUX_IN1_UC: IC1.40 (PE5(OC1B/XCK1/MOSI)), IC7.4 (O)
BNC_IOS_DIR: U2.2 (DIR), U3.3 (1Y)
BNC_IOS_ENBL: R15.2, U2.22 (OE), U3.6 (2B)
CLOCK_IN: CLKIN.4, IC1.21 (PC6(MISO/RXD1)), IC8.2 (I), R3.2
CLOCK_OUT: IC1.22 (PC7(SCK/TXD1/CLKO/EVO)), IC9.2 (I)
EN_CLOCK_IN: IC1.77 (PK2(A2/A10/A18)), IC8.1 (OE), R54.1
EN_CLOCK_OUT: IC1.76 (PK1(A1/A9/A17)), IC9.1 (OE), R55.1
FTDI_CTS: IC1.75 (PK0(A0/A8/A16)), IC3.11 (!CTS)
FTDI_RTS: IC1.71 (PJ6(A10/D6/A6/A14)), IC3.3 (!RTS)
FTDI_RXD: IC1.48 (PF3(OC0D/TXD0)), IC3.5 (RXD)
FTDI_TXD: IC1.47 (PF2(OC0C/RXD0)), IC3.1 (TXD)
GND: BNC0.2, BNC0.3 (2), BNC1.2, BNC1.3 (2), BNC2.2, BNC2.3 (2), BNC3.2, BNC3.3 (2), BNC4.2, BNC4.3 (2), C1.2, C2.2, C3.2, C4.2, C5.2, C6.2, C7.2, C9.2, C10.2, C11.2, C12.2, C13.2, C14.2, C15.2, C16.2, C17.2, C18.2, C19.2, C20.2, C21.2, C22.2, C23.2, C24.2, C25.2, C27.2, C28.2, C29.2, C30.2, C31.2, C32.2, C33.2, C34.2, C35.2, C36.2, C37.2, C38.2, C39.-, C40.2, C41.2, C42.2, C43.2, C44.2, C45.2, C46.2, C47.2, C48.2, C49.2, C50.2, C51.2, C52.2, CLKIN.5, GND_TP0.TP, GND_TP1.TP, IC1.3 (GND), IC1.13 (GND), IC1.23 (GND), IC1.33 (GND), IC1.43 (GND), IC1.53 (GND), IC1.63 (GND), IC1.73 (GND), IC1.84 (GND), IC1.93 (GND), IC2.P$2 (GND), IC3.7 (GND), IC3.18 (GND), IC3.21 (GND), IC3.25 (GND), IC3.26 (TEST), IC4.2 (GND), IC5.2 (GND), IC6.4 (AGND), IC7.1 (OE), IC7.3 (GND), IC8.3 (GND), IC9.3 (GND), IC10.1 (OE), IC10.3 (GND), OSC.P$2 (GND), PDI.6, R9.2, R10.2, R11.2, R12.2, R13.2, R14.1, R15.1, R16.2, R17.2, R19.1, R38.1, R43.1, R46.1, R47.1, R53.2, R54.2, R56.2, R57.2, R58.2, R59.2, R60.2, R61.2, R62.2, R63.2, R64.2, R65.2, R66.2, R67.2, R69.2, SV1.9, T2.2 (E), T3.2 (E), T4.2 (E), T5.2 (E), T6.2 (E), T7.2 (E), T8.2 (E), T9.2 (E), T10.2 (E), T11.2 (E), T12.2 (E), T13.2 (E), U1.11 (GND), U1.12 (GND), U1.13 (GND), U2.11 (GND), U2.12 (GND), U2.13 (GND), U3.1 (!1OE), U3.4 (!2OE), U3.7 (GND), U3.10 (!3OE), U3.13 (!4OE), USB.P$5 (5)
GND_ISO: C26.2, CLKOUT.5, IC6.5 (BGND)
IDE_IOS_DIR: U1.2 (DIR), U3.8 (3Y)
IDE_IOS_ENBL: R14.2, U1.22 (OE), U3.11 (4Y)
IO0: BNC0.1, R4.1, R19.2
IO0_UC: IC1.29 (PD4(OC1A/!SS!)), U2.21 (B0)
IO1: BNC1.1, R5.1, R38.2
IO1_UC: IC1.28 (PD3(OC0D/TXD0)), U2.20 (B1)
IO2: BNC2.1, R6.1, R43.2
IO2_UC: IC1.27 (PD2(OC0C/RXD0)), U2.19 (B2)
IO3: BNC3.1, R7.1, R46.2
IO3_UC: IC1.26 (PD1(OC0B/XCK0/SCL)), U2.18 (B3)
IO4: BNC4.1, R8.1, R47.2
IO4_UC: IC1.25 (PD0(OC0A/SDA)), U2.17 (B4)
IO5: R9.1, R48.1, SV1.1
IO5_UC: IC1.15 (PC0(OC0A/SDA)), U1.21 (B0)
IO6: R10.1, R49.1, SV1.2
IO6_UC: IC1.16 (PC1(OC0B/XCK0/SCL)), U1.20 (B1)
IO7: R11.1, R50.1, SV1.3
IO7_UC: IC1.17 (PC2(OC0C/RXD0)), U1.19 (B2)
IO8: R12.1, R51.1, SV1.4
IO8_UC: IC1.18 (PC3(OC0D/TXD0)), U1.18 (B3)
IO9: R13.1, R52.1, SV1.5
IO9_UC: IC1.35 (PE0(OC0A/SDA)), U1.17 (B4)
LED_I0: IC1.55 (PH0(!WE!)), R20.1
LED_I1: IC1.56 (PH1(!CAS!/!RE!)), R21.1
LED_I2: IC1.57 (PH2(!RAS!/ALE1)), R22.1
LED_I3: IC1.58 (PH3(!DOM!/ALE2)), R23.1
LED_I4: IC1.59 (PH4(BA0/!CS0!/A16)), R24.1
LED_I5: IC1.60 (PH5(BA1/!CS1!/A17)), R26.1
LED_I6: IC1.61 (PH6(CKE/!CS2!/A18)), R27.1
LED_I7: IC1.62 (PH7(CLK/!CS3!/A19)), R28.1
LED_I8: IC1.65 (PJ0(D0/A0/A8)), R29.1
LED_I9: IC1.66 (PJ1(D1/A1/A9)), R30.1
LED_PWR: IC1.67 (PJ2(D2/A2/A10)), R25.1
unnamed: R24.2, T10.1 (B)
unnamed: CLKOUT.4, IC6.6 (B1)
unnamed: R20.2, T2.1 (B)
unnamed: LED0.C2 (C), R32.1
unnamed: C26.1, CLKOUT.1, IC6.8 (BVDD)
unnamed: C50.1, R48.2, U1.3 (A0)
unnamed: R36.2, T10.3 (C)
unnamed: R32.2, T2.3 (C)
unnamed: IC1.38 (PE3(OC0D/TXD0)), R53.1
unnamed: R26.2, T3.1 (B)
unnamed: R22.2, T6.1 (B)
unnamed: R39.2, T3.3 (C)
unnamed: R21.2, T4.1 (B)
unnamed: LED3.C1 (C), R42.1
unnamed: R33.2, T4.3 (C)
unnamed: R27.2, T5.1 (B)
unnamed: R34.2, T6.3 (C)
unnamed: R40.2, T5.3 (C)
unnamed: LED3.C2 (C), R35.1
unnamed: R28.2, T7.1 (B)
unnamed: R41.2, T7.3 (C)
unnamed: R23.2, T8.1 (B)
unnamed: R35.2, T8.3 (C)
unnamed: R29.2, T9.1 (B)
unnamed: R42.2, T9.3 (C)
unnamed: LED1.C2 (C), R33.1
unnamed: LED2.C2 (C), R34.1
unnamed: LED1.C1 (C), R40.1
unnamed: LED2.C1 (C), R41.1
unnamed: R30.2, T11.1 (B)
unnamed: LED0.C1 (C), R39.1
unnamed: C7.1, IC3.17 (3V3OUT)
unnamed: IC2.P$1 (IO1), USB.P$2 (2)
unnamed: CLKIN.1, R2.2, R3.1
unnamed: C24.1, IC5.5 (OUT), R2.1
unnamed: IC6.2 (A1), IC8.4 (O), IC9.4 (O)
unnamed: R44.2, T11.3 (C)
unnamed: IC2.P$3 (IO2), USB.P$3 (3)
unnamed: R25.2, T12.1 (B)
unnamed: R37.2, T12.3 (C)
unnamed: R31.2, T13.1 (B)
unnamed: C2.1, USB.SHIELD_4
unnamed: R45.2, T13.3 (C)
unnamed: R69.1, USB.SHIELD_1
unnamed: LED5.C1 (C), R45.1
unnamed: LED5.C2 (C), R37.1
unnamed: LED4.C2 (C), R36.1
unnamed: LED4.C1 (C), R44.1
unnamed: C49.1, R49.2, U1.4 (A1)
unnamed: C48.1, R50.2, U1.5 (A2)
unnamed: C47.1, R51.2, U1.6 (A3)
unnamed: C46.1, R52.2, U1.7 (A4)
unnamed: C45.1, R4.2, U2.3 (A0)
unnamed: C44.1, R5.2, U2.4 (A1)
unnamed: C43.1, R6.2, U2.5 (A2)
unnamed: R61.1, U1.16 (B5)
unnamed: C42.1, R7.2, U2.6 (A3)
unnamed: R60.1, U1.15 (B6)
unnamed: R59.1, U1.14 (B7)
unnamed: R56.1, U1.10 (A7)
unnamed: C41.1, R8.2, U2.7 (A4)
unnamed: R57.1, U1.9 (A6)
unnamed: R58.1, U1.8 (A5)
unnamed: R62.1, U2.10 (A7)
unnamed: R63.1, U2.9 (A6)
unnamed: R64.1, U2.8 (A5)
unnamed: R67.1, U2.16 (B5)
unnamed: R66.1, U2.15 (B6)
unnamed: R65.1, U2.14 (B7)
OSC1: IC1.92 (PR1(XTAL1)), OSC.P$3 (OUTPUT)
PDI_CLK: C51.1, IC1.90 (PDI-CLK/!RESET), PDI.5, R68.1
PDI_DATA: IC1.89 (PDI-DATA), PDI.1
STATE: IC1.1 (PA6(ADCA6)), R31.1
USBDM: C6.1, IC2.P$6 (IO1), IC3.16 (USBDM)
USBDP: C4.1, IC2.P$4 (IO2), IC3.15 (USBDP)
U_BNC_IOS_DIR: IC1.32 (PD7(TXD1/SCK/CLKO/EVO)), U3.2 (1A)
U_BNC_IOS_ENBL: IC1.31 (PD6(RXD1/MISO)), U3.5 (2A)
U_IDE_IOS_DIR: IC1.10 (PB5(ADCB5/TDI)), U3.9 (3A)
U_IDE_IOS_ENBL: IC1.11 (PB6(ADCB6/TCK)), U3.12 (4A)

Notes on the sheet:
Vf = 2V We need ~5.5mA
8.5 mA max.
SBH11-PBPC-D05-RA-BK
R53 u IO-function selection
version control pin

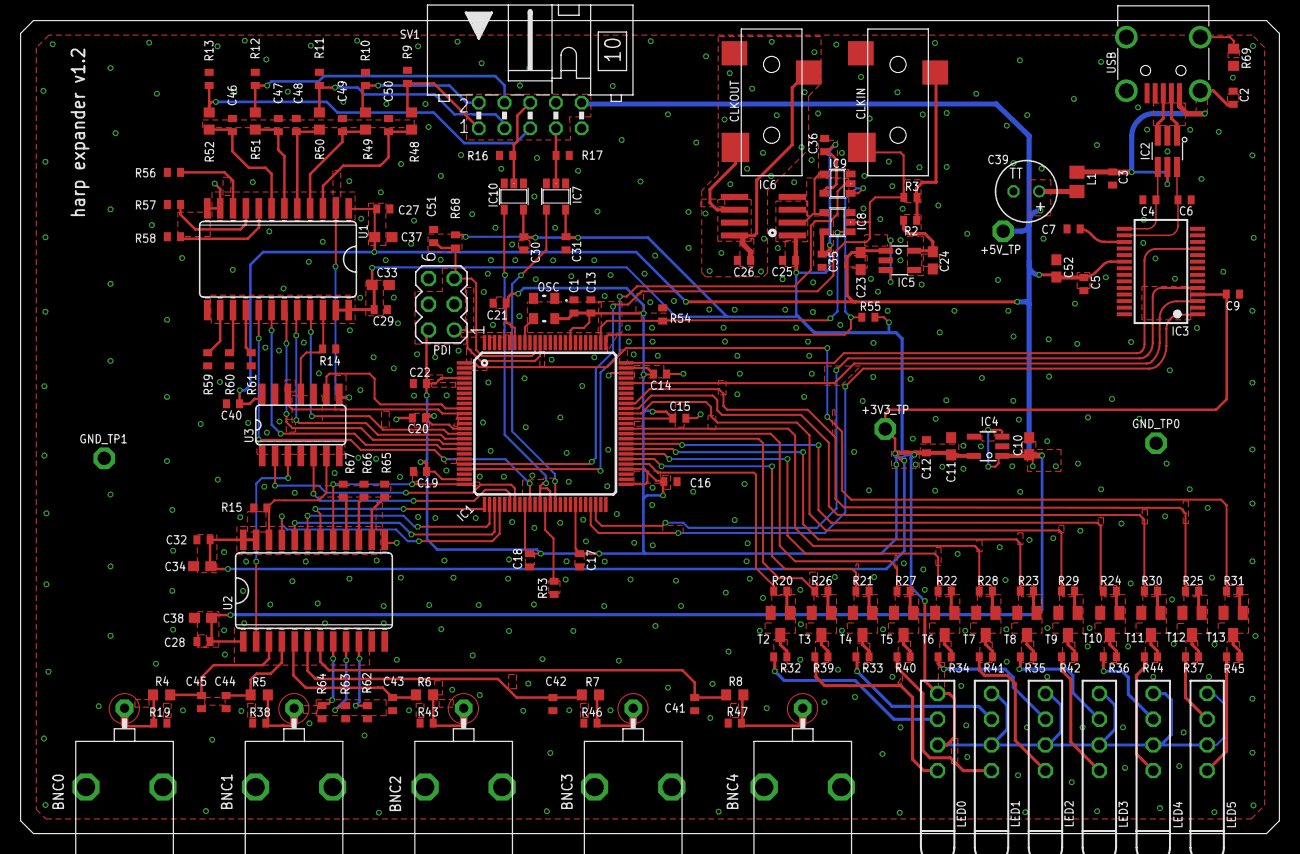
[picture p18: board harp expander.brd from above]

Board: 2 copper layers, 124.5 x 80.4 mm, 165 parts (0 on the bottom side), 131 nets.

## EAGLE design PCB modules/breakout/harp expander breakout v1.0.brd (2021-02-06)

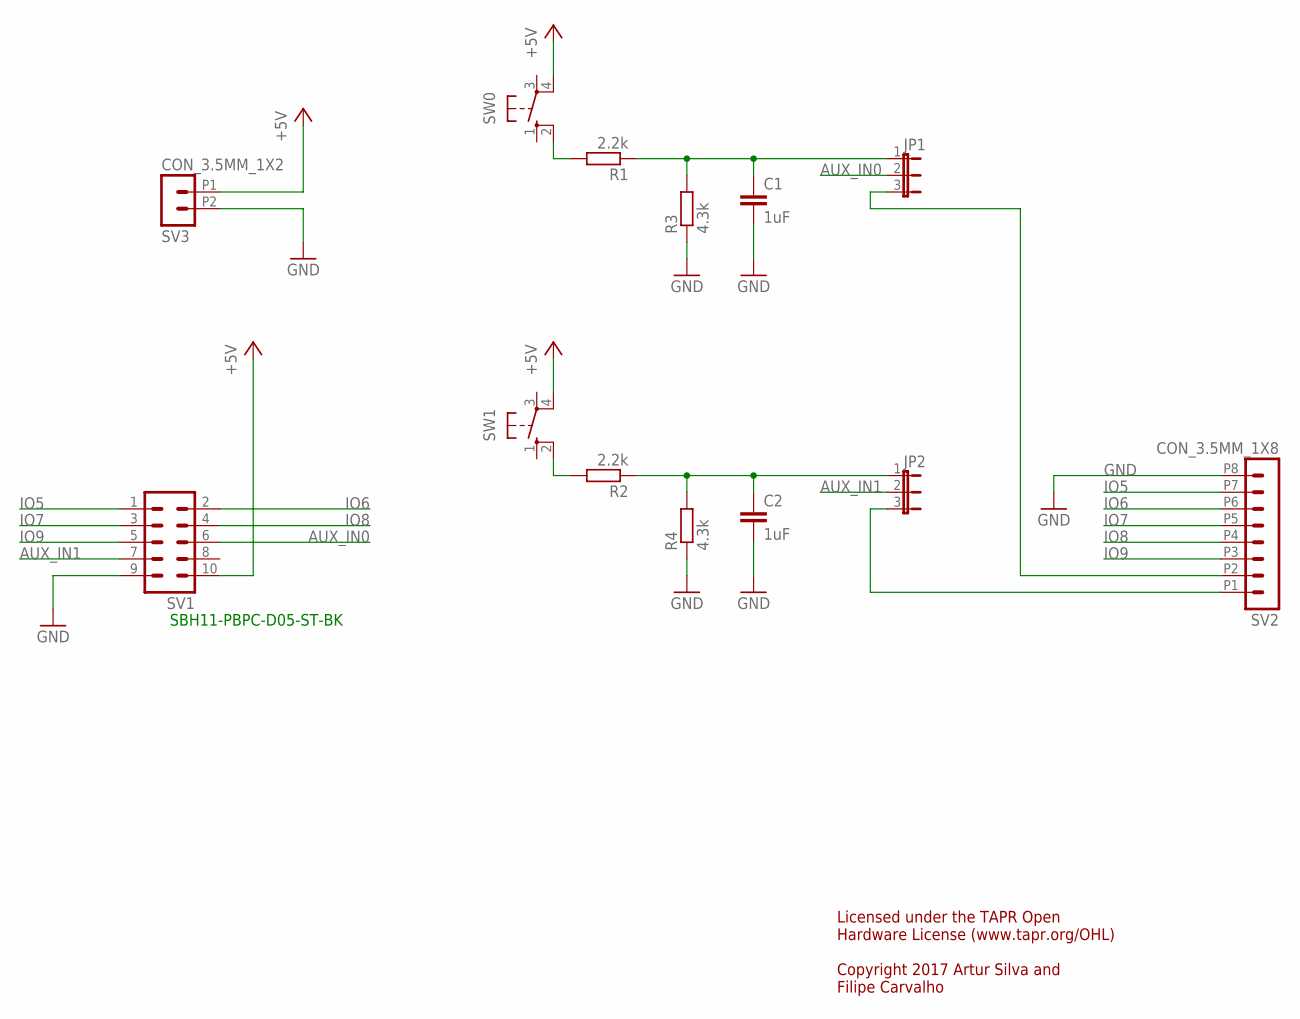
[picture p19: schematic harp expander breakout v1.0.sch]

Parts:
C1, C2: 1uF; C0603
JP1, JP2: JP2E; JP2
R1, R2: 2.2k; R0603
R3, R4: 4.3k; R0603
SV1: ML10
SV2: CON_3.5MM_1X8
SV3: CON_3.5MM_1X2
SW0: 40-XX; B3F-40XX; MPN B3F-4000
SW1: 40-XX; B3F-40XX

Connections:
+5V: SV1.10, SV3.P1 (1), SW0.4 (P1), SW1.4 (P1)
AUX_IN0: JP1.2, SV1.6
AUX_IN0_CONNECTOR: JP1.3, SV2.P2 (2)
AUX_IN1: JP2.2, SV1.7
AUX_IN1_CONNECTOR: JP2.3, SV2.P1 (1)
GND: C1.2, C2.2, R3.1, R4.1, SV1.9, SV2.P8 (8), SV3.P2 (2)
IO5: SV1.1, SV2.P7 (7)
IO6: SV1.2, SV2.P6 (6)
IO7: SV1.3, SV2.P5 (5)
IO8: SV1.4, SV2.P4 (4)
IO9: SV1.5, SV2.P3 (3)
unnamed: R2.2, SW1.2 (S1)
unnamed: C2.1, JP2.1, R2.1, R4.2
unnamed: R1.2, SW0.2 (S1)
unnamed: C1.1, JP1.1, R1.1, R3.2

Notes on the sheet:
Licensed under the TAPR Open Hardware License (www.tapr.org/OHL) Copyright 2017 Artur Silva and Filipe Carvalho
SBH11-PBPC-D05-ST-BK

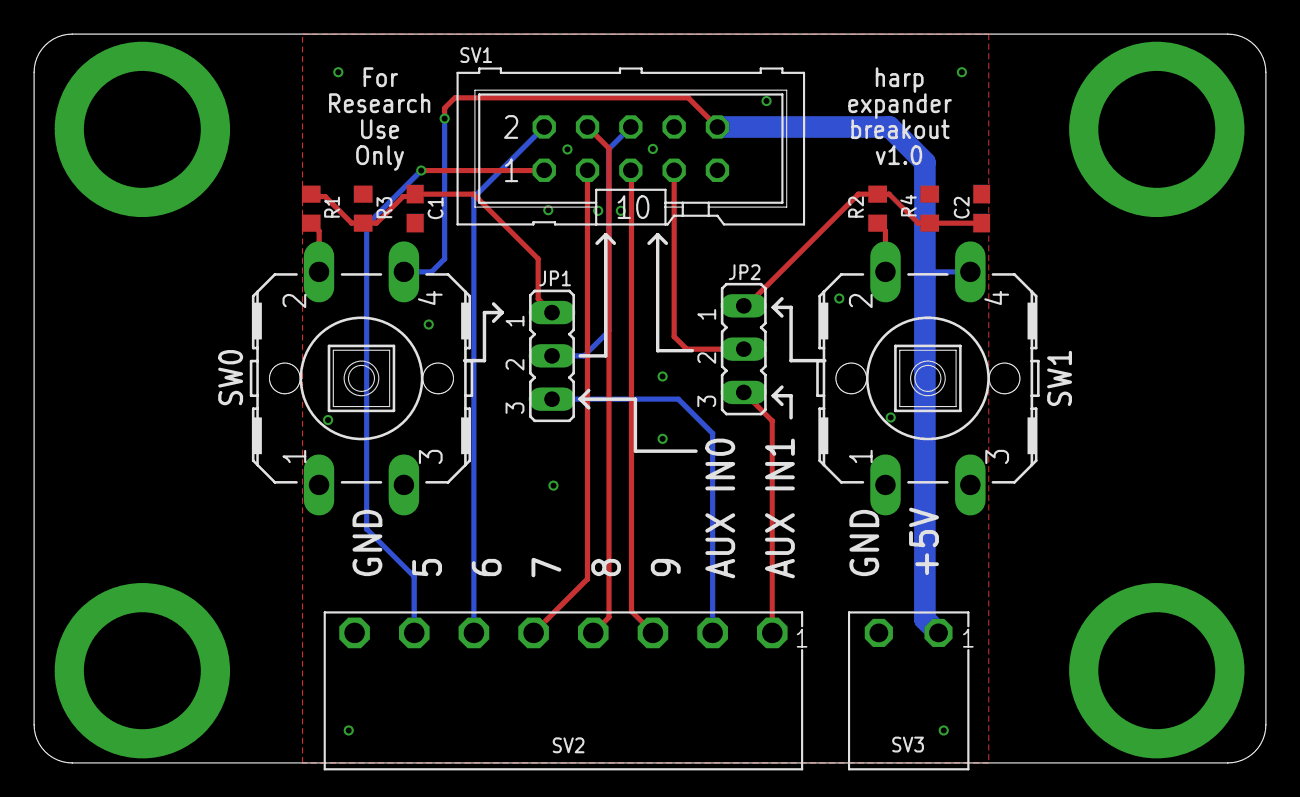
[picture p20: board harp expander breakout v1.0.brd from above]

Board: 2 copper layers, 72.2 x 42.8 mm, 13 parts (0 on the bottom side), 15 nets.

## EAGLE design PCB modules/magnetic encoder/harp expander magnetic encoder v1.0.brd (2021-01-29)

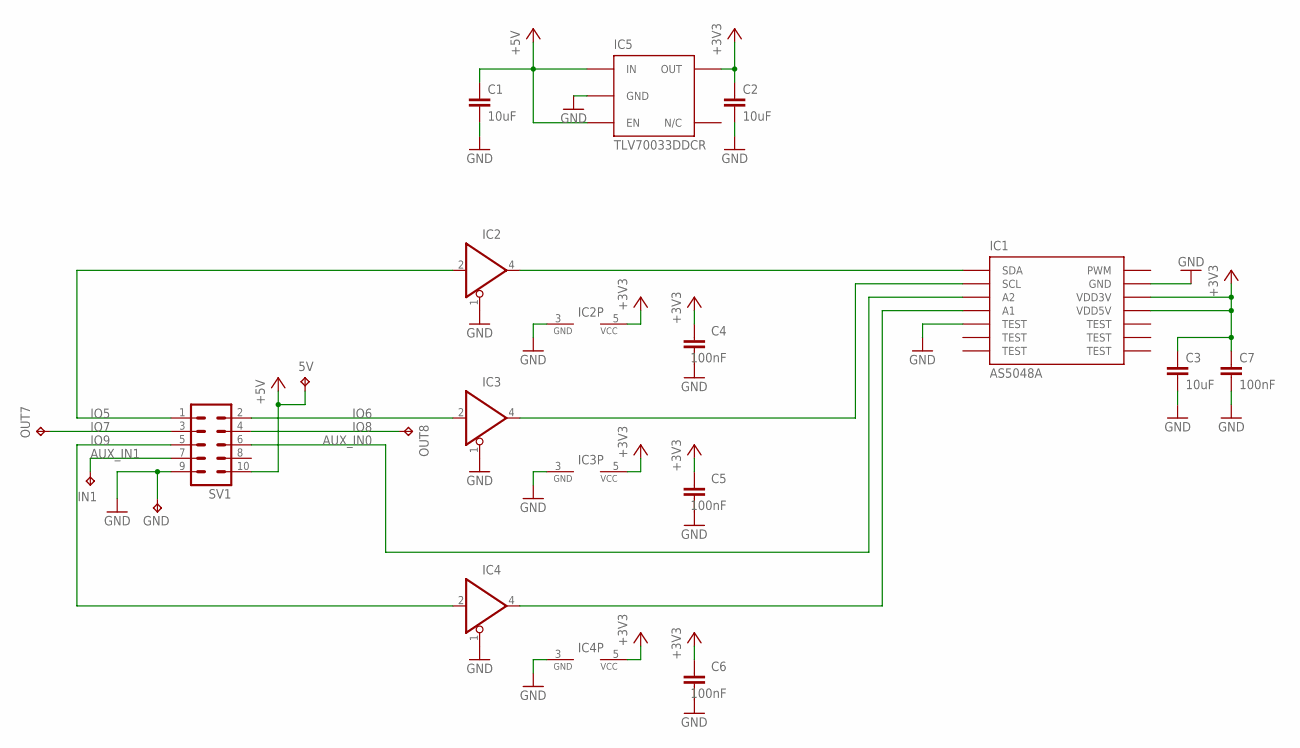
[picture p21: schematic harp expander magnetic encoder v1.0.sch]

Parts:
5V: TPPAD1-13; P1-13
C1, C2, C3: 10uF; C0603; MPN C1608X6S1C475K080AC
C4, C5, C6, C7: 100nF; C0402; MPN MC0402B104K160CT
GND: TPPAD1-13; P1-13
IC1: AS5048A; TSSOP-14
IC2, IC3, IC4: SN74LVC1G125DBVT; SOT23-5; MPN SN74LVC1G125DBVT
IC5: TLV70033DDCR; TSOT23-5; MPN TLV70033DDCR
IN1: TPPAD1-13; P1-13
OUT7, OUT8: TPPAD1-13; P1-13
SV1: ML10

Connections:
!CS: IC1.1 (SDA), IC2.4 (O)
+3V3: C2.1, C3.1, C4.1, C5.1, C6.1, C7.1, IC1.11 (VDD5V), IC1.12 (VDD3V), IC2.5 (VCC), IC3.5 (VCC), IC4.5 (VCC), IC5.5 (OUT)
+5V: 5V.TP, C1.1, IC5.1 (IN), IC5.3 (EN), SV1.10
AUX_IN0: IC1.3 (A2), SV1.6
AUX_IN1: IN1.TP, SV1.7
CLK: IC1.2 (SCL), IC3.4 (O)
GND: C1.2, C2.2, C3.2, C4.2, C5.2, C6.2, C7.2, GND.TP, IC1.5 (TEST), IC1.13 (GND), IC2.1 (OE), IC2.3 (GND), IC3.1 (OE), IC3.3 (GND), IC4.1 (OE), IC4.3 (GND), IC5.2 (GND), SV1.9
IO5: IC2.2 (I), SV1.1
IO6: IC3.2 (I), SV1.2
IO7: OUT7.TP, SV1.3
IO8: OUT8.TP, SV1.4
IO9: IC4.2 (I), SV1.5
MOSI: IC1.4 (A1), IC4.4 (O)

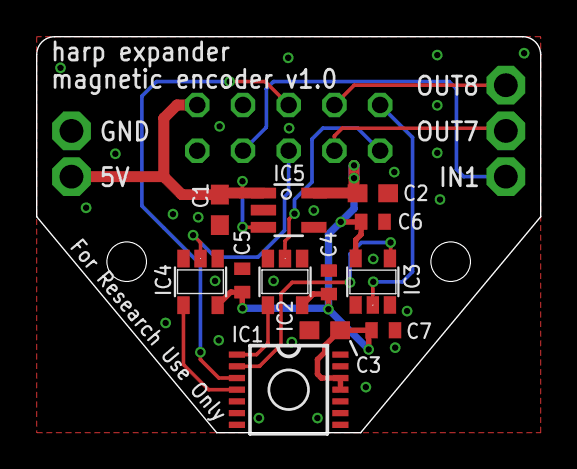
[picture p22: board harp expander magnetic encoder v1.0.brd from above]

Board: 2 copper layers, 28.0 x 22.0 mm, 18 parts (1 on the bottom side), 13 nets.

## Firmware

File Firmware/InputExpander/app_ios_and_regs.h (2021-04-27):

#ifndef _APP_IOS_AND_REGS_H_
#define _APP_IOS_AND_REGS_H_
#include "cpu.h"

void init_ios(void);
/************************************************************************/
/* Definition of input pins                                             */
/************************************************************************/
// AUX_INPUT0             Description: Auxiliary input 0
// AUX_INPUT1             Description: Auxiliary input 1
// IS_INPUT               Description: Check for the right hardware
// IN0                    Description: Input 0
// IN1                    Description: Input 1
// IN2                    Description: Input 2
// IN3                    Description: Input 3
// IN4                    Description: Input 4
// IN5                    Description: Input 5
// IN6                    Description: Input 6
// IN7                    Description: Input 7
// IN8                    Description: Input 8
// IN9                    Description: Input 9
// PA0                    Description: 
// PA1                    Description: 
// PA2                    Description: 
// PA3                    Description: 
// PA4                    Description: 
// PA5                    Description: 
// PA7                    Description: 
// PB0                    Description: 
// PB1                    Description: 
// PB2                    Description: 
// PB3                    Description: 
// PB4                    Description: 
// PB7                    Description: 
// PC4                    Description: 
// PC5                    Description: 
// PD5                    Description: 
// PE1                    Description: 
// PE6                    Description: 
// PE7                    Description: 
// PF0                    Description: 
// PF1                    Description: 
// PF4                    Description: 
// PF5                    Description: 
// PF6                    Description: 
// PF7                    Description: 
// PJ3                    Description: 
// PJ4                    Description: 
// PJ5                    Description: 
// PJ7                    Description: 
// PK3                    Description: 
// PK4                    Description: 
// PK5                    Description: 
// PK6                    Description: 
// PK7                    Description: 
// PQ0                    Description: 
// PQ1                    Description: 
// PQ2                    Description: 
// PQ3                    Description: 

#define read_AUX_INPUT0 read_io(PORTE, 2)       // AUX_INPUT0
#define read_AUX_INPUT1 read_io(PORTE, 5)       // AUX_INPUT1
#define read_IS_INPUT read_io(PORTE, 3)         // IS_INPUT
#define read_IN0 read_io(PORTD, 4)              // IN0
#define read_IN1 read_io(PORTD, 3)              // IN1
#define read_IN2 read_io(PORTD, 2)              // IN2
#define read_IN3 read_io(PORTD, 1)              // IN3
#define read_IN4 read_io(PORTD, 0)              // IN4
#define read_IN5 read_io(PORTC, 0)              // IN5
#define read_IN6 read_io(PORTC, 1)              // IN6
#define read_IN7 read_io(PORTC, 2)              // IN7
#define read_IN8 read_io(PORTC, 3)              // IN8
#define read_IN9 read_io(PORTE, 0)              // IN9
#define read_PA0 read_io(PORTA, 0)              // PA0
#define read_PA1 read_io(PORTA, 1)              // PA1
#define read_PA2 read_io(PORTA, 2)              // PA2
#define read_PA3 read_io(PORTA, 3)              // PA3
#define read_PA4 read_io(PORTA, 4)              // PA4
#define read_PA5 read_io(PORTA, 5)              // PA5
#define read_PA7 read_io(PORTA, 7)              // PA7
#define read_PB0 read_io(PORTB, 0)              // PB0
#define read_PB1 read_io(PORTB, 1)              // PB1
#define read_PB2 read_io(PORTB, 2)              // PB2
#define read_PB3 read_io(PORTB, 3)              // PB3
#define read_PB4 read_io(PORTB, 4)              // PB4
#define read_PB7 read_io(PORTB, 7)              // PB7
#define read_PC4 read_io(PORTC, 4)              // PC4
#define read_PC5 read_io(PORTC, 5)              // PC5
#define read_PD5 read_io(PORTD, 5)              // PD5
#define read_PE1 read_io(PORTE, 1)              // PE1
#define read_PE6 read_io(PORTE, 6)              // PE6
#define read_PE7 read_io(PORTE, 7)              // PE7
#define read_PF0 read_io(PORTF, 0)              // PF0
#define read_PF1 read_io(PORTF, 1)              // PF1
#define read_PF4 read_io(PORTF, 4)              // PF4
#define read_PF5 read_io(PORTF, 5)              // PF5
#define read_PF6 read_io(PORTF, 6)              // PF6
#define read_PF7 read_io(PORTF, 7)              // PF7
#define read_PJ3 read_io(PORTJ, 3)              // PJ3
#define read_PJ4 read_io(PORTJ, 4)              // PJ4
#define read_PJ5 read_io(PORTJ, 5)              // PJ5
#define read_PJ7 read_io(PORTJ, 7)              // PJ7
#define read_PK3 read_io(PORTK, 3)              // PK3
#define read_PK4 read_io(PORTK, 4)              // PK4
#define read_PK5 read_io(PORTK, 5)              // PK5
#define read_PK6 read_io(PORTK, 6)              // PK6
#define read_PK7 read_io(PORTK, 7)              // PK7
#define read_PQ0 read_io(PORTQ, 0)              // PQ0
#define read_PQ1 read_io(PORTQ, 1)              // PQ1
#define read_PQ2 read_io(PORTQ, 2)              // PQ2
#define read_PQ3 read_io(PORTQ, 3)              // PQ3

/************************************************************************/
/* Definition of output pins                                            */
/************************************************************************/
// LED_0                  Description: Drives the I0 LED
// LED_1                  Description: Drives the I1 LED
// LED_2                  Description: Drives the I2 LED
// LED_3                  Description: Drives the I3 LED
// LED_4                  Description: Drives the I4 LED
// LED_5                  Description: Drives the I5 LED
// LED_6                  Description: Drives the I6 LED
// LED_7                  Description: Drives the I7 LED
// LED_8                  Description: Drives the I8 LED
// LED_9                  Description: Drives the I9 LED
// LED_PWR                Description: Drives the PWR LED
// LED_STATE              Description: Drives the STATE LED
// IDE_IOS_DIR            Description: Direction control
// IDE_IOS_EN             Description: Buffer enable
// BNC_IOS_DIR            Description: Direction control
// BNC_IOS_EN             Description: Buffer enable

/* LED_0 */
#define set_LED_0 set_io(PORTH, 0)
#define clr_LED_0 clear_io(PORTH, 0)
#define tgl_LED_0 toggle_io(PORTH, 0)
#define read_LED_0 read_io(PORTH, 0)

/* LED_1 */
#define set_LED_1 set_io(PORTH, 1)
#define clr_LED_1 clear_io(PORTH, 1)
#define tgl_LED_1 toggle_io(PORTH, 1)
#define read_LED_1 read_io(PORTH, 1)

/* LED_2 */
#define set_LED_2 set_io(PORTH, 2)
#define clr_LED_2 clear_io(PORTH, 2)
#define tgl_LED_2 toggle_io(PORTH, 2)
#define read_LED_2 read_io(PORTH, 2)

/* LED_3 */
#define set_LED_3 set_io(PORTH, 3)
#define clr_LED_3 clear_io(PORTH, 3)
#define tgl_LED_3 toggle_io(PORTH, 3)
#define read_LED_3 read_io(PORTH, 3)

/* LED_4 */
#define set_LED_4 set_io(PORTH, 4)
#define clr_LED_4 clear_io(PORTH, 4)
#define tgl_LED_4 toggle_io(PORTH, 4)
#define read_LED_4 read_io(PORTH, 4)

/* LED_5 */
#define set_LED_5 set_io(PORTH, 5)
#define clr_LED_5 clear_io(PORTH, 5)
#define tgl_LED_5 toggle_io(PORTH, 5)
#define read_LED_5 read_io(PORTH, 5)

/* LED_6 */
#define set_LED_6 set_io(PORTH, 6)
#define clr_LED_6 clear_io(PORTH, 6)
#define tgl_LED_6 toggle_io(PORTH, 6)
#define read_LED_6 read_io(PORTH, 6)

/* LED_7 */
#define set_LED_7 set_io(PORTH, 7)
#define clr_LED_7 clear_io(PORTH, 7)
#define tgl_LED_7 toggle_io(PORTH, 7)
#define read_LED_7 read_io(PORTH, 7)

/* LED_8 */
#define set_LED_8 set_io(PORTJ, 0)
#define clr_LED_8 clear_io(PORTJ, 0)
#define tgl_LED_8 toggle_io(PORTJ, 0)
#define read_LED_8 read_io(PORTJ, 0)

/* LED_9 */
#define set_LED_9 set_io(PORTJ, 1)
#define clr_LED_9 clear_io(PORTJ, 1)
#define tgl_LED_9 toggle_io(PORTJ, 1)
#define read_LED_9 read_io(PORTJ, 1)

/* LED_PWR */
#define set_LED_PWR set_io(PORTJ, 2)
#define clr_LED_PWR clear_io(PORTJ, 2)
#define tgl_LED_PWR toggle_io(PORTJ, 2)
#define read_LED_PWR read_io(PORTJ, 2)

/* LED_STATE */
#define set_LED_STATE set_io(PORTA, 6)
#define clr_LED_STATE clear_io(PORTA, 6)
#define tgl_LED_STATE toggle_io(PORTA, 6)
#define read_LED_STATE read_io(PORTA, 6)

/* IDE_IOS_DIR */
#define set_IDE_IOS_DIR set_io(PORTB, 5)
#define clr_IDE_IOS_DIR clear_io(PORTB, 5)
#define tgl_IDE_IOS_DIR toggle_io(PORTB, 5)
#define read_IDE_IOS_DIR read_io(PORTB, 5)

/* IDE_IOS_EN */
#define set_IDE_IOS_EN set_io(PORTB, 6)
#define clr_IDE_IOS_EN clear_io(PORTB, 6)
#define tgl_IDE_IOS_EN toggle_io(PORTB, 6)
#define read_IDE_IOS_EN read_io(PORTB, 6)

/* BNC_IOS_DIR */
#define set_BNC_IOS_DIR set_io(PORTD, 7)
#define clr_BNC_IOS_DIR clear_io(PORTD, 7)
#define tgl_BNC_IOS_DIR toggle_io(PORTD, 7)
#define read_BNC_IOS_DIR read_io(PORTD, 7)

/* BNC_IOS_EN */
#define set_BNC_IOS_EN set_io(PORTD, 6)
#define clr_BNC_IOS_EN clear_io(PORTD, 6)
#define tgl_BNC_IOS_EN toggle_io(PORTD, 6)
#define read_BNC_IOS_EN read_io(PORTD, 6)


/************************************************************************/
/* Registers' structure                                                 */
/************************************************************************/
typedef struct
{
	uint8_t REG_AUX_INPUTS;
	uint8_t REG_AUX_INPUTS_RISING_EDGE_ENABLE;
	uint8_t REG_AUX_INPUTS_FALLING_EDGE_ENABLE;
	uint16_t REG_INPUTS[2];
	uint16_t REG_RISING_EDGE_ENABLE;
	uint16_t REG_FALLING_EDGE_ENABLE;
	uint8_t REG_INPUT_MODE;
	uint8_t REG_ENCODER_MODE;
	int16_t REG_ENCODER;
	uint8_t REG_EXPANSION_OPTIONS;
} AppRegs;

/************************************************************************/
/* Registers' address                                                   */
/************************************************************************/
/* Registers */
#define ADD_REG_AUX_INPUTS                  32 // U8     State of the auxiliary inputs
#define ADD_REG_AUX_INPUTS_RISING_EDGE_ENABLE 33 // U8     Enables the rising edge detection of the correspondet auxiliar input (bitmask)
#define ADD_REG_AUX_INPUTS_FALLING_EDGE_ENABLE 34 // U8     Enables the falling edge detection of the correspondet auxiliar input (bitmask)
#define ADD_REG_INPUTS                      35 // U16    State of the inputs [0] , change masks [1]
#define ADD_REG_RISING_EDGE_ENABLE          36 // U16    Enables the rising edge detection of the correspondet input (bitmask)
#define ADD_REG_FALLING_EDGE_ENABLE         37 // U16    Enables the falling edge detection of the correspondet input (bitmask)
#define ADD_REG_INPUT_MODE                  38 // U8     Configures the input mode
#define ADD_REG_ENCODER_MODE                39 // U8     Configures the rotary encoder
#define ADD_REG_ENCODER                     40 // I16    Contains the rotary encoder reading
#define ADD_REG_EXPANSION_OPTIONS           41 // U8     Selects the current expansion board available in the EXPANSION port

/************************************************************************/
/* PWM Generator registers' memory limits                               */
/*                                                                      */
/* DON'T change the APP_REGS_ADD_MIN value !!!                          */
/* DON'T change these names !!!                                         */
/************************************************************************/
/* Memory limits */
#define APP_REGS_ADD_MIN                    0x20
#define APP_REGS_ADD_MAX                    0x29
#define APP_NBYTES_OF_REG_BANK              16
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

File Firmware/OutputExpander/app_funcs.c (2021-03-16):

#include "app_funcs.h"
#include "app_ios_and_regs.h"
#include "hwbp_core.h"


/************************************************************************/
/* Create pointers to functions                                         */
/************************************************************************/
extern AppRegs app_regs;

void (*app_func_rd_pointer[])(void) = {
	&app_read_REG_AUX_INPUTS,
	&app_read_REG_AUX_INPUTS_RISING_EDGE_ENABLE,
	&app_read_REG_AUX_INPUTS_FALLING_EDGE_ENABLE,
	&app_read_REG_OUTPUTS_SET,
	&app_read_REG_OUTPUTS_CLEAR,
	&app_read_REG_OUTPUTS_TOGGLE,
	&app_read_REG_OUTPUTS_WRITE,
	&app_read_REG_PWM_AND_STIM_ENABLE,
	&app_read_REG_PWM_AND_STIM_DISABLE,
	&app_read_REG_PWM_AND_STIM_WRITE,
	&app_read_REG_PWM0_FREQ,
	&app_read_REG_PWM0_DUTYCYCLE,
	&app_read_REG_PWM0_COUNT,
	&app_read_REG_PWM0_REAL_FREQ,
	&app_read_REG_PWM0_REAL_DUTYCYCLE,
	&app_read_REG_PWM0_MODE,
	&app_read_REG_PWM0_TRIG,
	&app_read_REG_PWM0_CONF_EVENT,
	&app_read_REG_PWM1_FREQ,
	&app_read_REG_PWM1_DUTYCYCLE,
	&app_read_REG_PWM1_COUNT,
	&app_read_REG_PWM1_REAL_FREQ,
	&app_read_REG_PWM1_REAL_DUTYCYCLE,
	&app_read_REG_PWM1_MODE,
	&app_read_REG_PWM1_TRIG,
	&app_read_REG_PWM1_CONF_EVENT,
	&app_read_REG_PWM2_FREQ,
	&app_read_REG_PWM2_DUTYCYCLE,
	&app_read_REG_PWM2_COUNT,
	&app_read_REG_PWM2_REAL_FREQ,
	&app_read_REG_PWM2_REAL_DUTYCYCLE,
	&app_read_REG_PWM2_MODE,
	&app_read_REG_PWM2_TRIG,
	&app_read_REG_PWM2_CONF_EVENT,
	&app_read_REG_PWM_START,
	&app_read_REG_PWM_STOP,
	&app_read_REG_PWM_RISE_EVENT,
	&app_read_REG_STIM0_T_ON,
	&app_read_REG_STIM0_T_OFF,
	&app_read_REG_STIM0_COUNT,
	&app_read_REG_STIM0_MODE,
	&app_read_REG_STIM0_TRIG,
	&app_read_REG_STIM_START,
	&app_read_REG_STIM_STOP,
	&app_read_REG_PULSE_ENABLE,
	&app_read_REG_PULSE_OUT0,
	&app_read_REG_PULSE_OUT1,
	&app_read_REG_PULSE_OUT2,
	&app_read_REG_PULSE_OUT3,
	&app_read_REG_PULSE_OUT4,
	&app_read_REG_PULSE_OUT5,
	&app_read_REG_PULSE_OUT6,
	&app_read_REG_PULSE_OUT7,
	&app_read_REG_PULSE_OUT8,
	&app_read_REG_PULSE_OUT9,
	&app_read_REG_EXPANSION_OPTIONS,
	&app_read_REG_RESERVED2,
	&app_read_REG_RESERVED3,
	&app_read_REG_MAG_ENCODER_READ,
	&app_read_REG_MAG_ENCODER_MODE,
	&app_read_REG_RESERVED4,
	&app_read_REG_RESERVED5,
	&app_read_REG_SERVO_PERIOD_US,
	&app_read_REG_SERVO0_PULSE_US,
	&app_read_REG_SERVO1_PULSE_US,
	&app_read_REG_SERVO2_PULSE_US
};
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

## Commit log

2020-10-18 Added the first PCB files.
    [harp input expander.brd, harp input expander.sch]
2020-10-31 Updated design files to the latest version.
    [harp expander.brd, harp expander.sch, harp input expander.brd]
2020-10-31 Added gerbers, centroids and BOM.
    [harp expander BOM.xlsx]
2020-10-31 Added panels and production files.
    [harp expander rear panel.brd, harp input expander front panel.brd, harp output expander front panel.brd]
2020-11-04 Corrected rear panel's silk screen.
    [harp expander rear panel.brd]
2020-11-04 Added panels' gerber files.
    [copper_bottom.gbr, copper_top.gbr, gerber_job.gbrjob, profile.gbr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]
2020-11-06 First firmware files.
    [registers.xls]
2020-11-15 Minor corrections.
    [harp expander.brd, harp expander.sch]
2020-11-15 Added breakout v1.0.
    [harp expander breakout BOM.xlsx, harp expander breakout v1.0.brd, harp expander breakout v1.0.sch]
2020-11-15 Updated BOM.
    [harp expander breakout BOM.xlsx]
2020-11-16 Corrected pinout.
    [registers.xls]
2020-11-21 Corrected silkscreen and minor change to top layer.
    [harp expander breakout BOM.xlsx, harp expander breakout v1.0.brd, harp expander breakout v1.0.sch]
2020-12-19 Added ability to connect to a Teensy/Arduino and to read rotary encoders.
    [harp expander.brd, harp expander.sch]
2020-12-19 Added ability to be used as a clock generator.
    [harp expander BOM.xlsx, harp expander.brd, harp expander.sch]
2020-12-19 Minor corrections on layout and schematics.
    [harp expander.brd, harp expander.sch]
2020-12-19 Updated production files.
    [harp expander BOM_simplified.xlsx]
2020-12-20 Minor corrections to BOMs.
    [harp expander BOM.xlsx, harp expander breakout BOM.xlsx, harp expander breakout BOM_simplified.xlsx]
2021-01-02 Realocate interrupt pins to latest schematic.
    [registers.xls]
2021-01-02 Corrected wrong buttons polarity.
    [harp expander breakout BOM.xlsx, harp expander breakout BOM_simplified.xlsx, harp expander breakout v1.0.brd, harp expander breakout v1.0.sch]
2021-01-29 Updated files for final revision before production.
    [harp expander breakout BOM.xlsx, harp expander breakout BOM_simplified.xlsx, harp expander breakout v1.0.brd, harp expander breakout v1.0.sch]
2021-01-29 Added first magnetic encoder files.
    [harp expander magnetic encoder v1.0 BOM.xlsx, harp expander magnetic encoder v1.0.brd, harp expander magnetic encoder v1.0.sch]
2021-01-29 Included mechanical details for 3D design.
    [harp expander magnetic encoder v1.0 - bottom.dxf, harp expander magnetic encoder v1.0 - top.dxf]
2021-01-29 Updated files for final revision.
    [harp expander servo driver v1.0 BOM.xlsx, harp expander servo driver v1.0.brd, harp expander servo driver v1.0.sch]
2021-02-06 Updated for the first functional code (some features still to implement).
    [registers.xls, registers_input.xls, registers_output.xls]
2021-02-06 Increased distance between screw connectors.
    [harp expander breakout v1.0.brd]
2021-02-06 Released the expander breakout PCB (v1.0).
2021-02-06 Implemented LED management.
2021-02-07 Corrected visualization and implemented the magnetic encoder expansion.
    [registers_input.xls, registers_output.xls]
2021-02-07 Added code to control the expander servo driver.
    [registers_input.xls, registers_output.xls]
2021-02-11 Changed the audio cable PN.
    [harp expander BOM.xlsx]
2021-02-11 Released expander magnetic encoder and updated expander breakout.
    [harp expander magnetic encoder v1.0 BOM.xlsx]
2021-02-11 Minor updates.
    [harp expander servo driver v1.0 BOM.xlsx, harp expander servo driver v1.0.brd, harp expander servo driver v1.0.sch]
2021-02-11 Replaced oscillator with a more precise one.
    [harp expander BOM.xlsx, harp expander BOM_simplified.xlsx]
2021-02-11 Added library and updated BOM.
    [harp expander servo driver v1.0 BOM.xlsx]
2021-02-16 Minor corrections to registers' descriptions.
    [registers_input.xls, registers_output.xls]
2021-02-16 Corrected bad timing when using the servo expander.
2021-02-21 Reversed the hardware's resistor assembly.
2021-02-21 Correct bad servo driver configuration.
2021-02-23 Added default for the magnetic encoder sample rate.
2021-02-24 Corrected device's ID.
2021-03-04 Add Bonsai interface for harp expander devices
2021-03-05 Added a new version that corrects a supply noise issue and re-arranged the connector's pinout.
    [harp expander servo driver v1.1.brd, harp expander servo driver v1.1.sch]
2021-03-07 Implemented ability to filter selected transitions on both auxiliary input lines.
    [registers_input.xls, registers_output.xls]
2021-03-07 Added new registers to control PWM and stimulation.
    [registers_output.xls]
2021-03-07 increased firmware version to 2.0.
    [registers_input.xls, registers_output.xls]
2021-03-08 Renamed STIM registers and added PULSE registers.
    [registers_output.xls]
2021-03-08 Implemented the ability to produce up to 3 different PWMs.
    [registers_output.xls]
2021-03-16 Added more flexibility to enable and disable PWM.
    [registers_output.xls]
2021-03-23 Add support for configuring expansion board modes
2021-04-24 Added filtering on inputs and reset lines to prevent erroneous behavior in noisy environments.
    [harp expander BOM.xlsx, harp expander BOM_simplified.xlsx, harp expander servo driver v1.1.brd, harp expander servo driver v1.1.sch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]
2021-04-24 Added a photo of the assembled device.
2021-04-27 Added ability to read a rotary encoder.
    [registers_input.xls, registers_output.xls]
2021-05-13 Minor BOM correction.
    [harp expander BOM.xlsx]
2021-06-01 Added version 1.2 of servo driver module.
    [harp expander servo driver v1.1 BOM.xlsx, harp expander servo driver v1.2 BOM.xlsx, harp expander servo driver v1.2.brd, harp expander servo driver v1.2.sch]
